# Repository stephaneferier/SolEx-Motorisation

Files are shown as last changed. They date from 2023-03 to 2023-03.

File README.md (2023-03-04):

# SolEx Motorisation (English version below)

Le Sol'Ex de Christian Buil est un "Explorateur solaire" qui permet d'imager le soleil dans une longueur d'onde souhaitée, allant du proche UV au proche IR.
La construction de ce spectroscope est détaillée sur son site internet: http://www.astrosurf.com/solex/sol-ex-objet.html
La partie traitement informatique du signal enregistré est confiée soit à i-Spec (programme écrit par Christian Buil), soit par Inti, programme développé par Valérie Desnoux. Ces deux programmes sont référencés sur le site Sol'Ex, et des mises à jour régulières sont publiées.
Un forum d'échange est aussi disponible à l'adresse : https://groups.io/g/Solex-project La communauté y est très active.

Nous vous présentons ici un appendice développé conjointement par Jean Brunet et Stéphane Ferier, qui permet de motoriser le Sol'Ex initial.
Le but ici est d'apporter une facilité à voyager parmi les raies spectrales qui composent le spectre solaire, au moyen d'un software développé pour Android/IOS, basé sur une page web gérée par le software. Des raies spectrales d'intérêt majeur y sont définies, et accessibles d'un simple clic. Le software permet outre les raies pré-programmées de sélectionner une longueur d'onde souhaitée et de demander au moteur d'orienter le réseau sur cette longueur d'onde. A l'inverse, il est aussi possible de visualiser une longueur d'onde (par retour de caméra d'acquisition), et de l'identifier sur l'affichage de la page web.

Le programme ainsi que les fichiers .stl de construction du support de motorisation sont "open-source", et toute amélioration est la bienvenue.
A cet effet, le fichier .rar contient tout le matériel nécessaire, y compris un fichier excel qui permet de trouver les paramètres de droite standard d'étalonnage.
En effet, le matériel fourni est optimisé pour un réseau de diffraction de 2400tr/mm; optiques 80/125mm constituant le Sol'Ex, ainsi que pour des roues dentées de motorisation d'un rapport de démultiplication 16 et 60 (GT-2) soit 3.75x. Si l'on souhaite utiliser un autre rapport, la droite d'étalonnage doit être adaptée en conséquence.

Outre le fichier .rar, vous trouverez aussi un fichier .pdf qui décrit en détails comment réaliser cette motorisation, comment monter le système sur le Sol'Ex, comment réaliser le montage électronique de pilotage, comment uploader le software dans l'ESP32 utilisé, ainsi que coment utiliser le software. Ce fichier .pdf est disponible en Français, et en Anglais.

# SolEx Motorization (English Version)

Christian Buil's Sol'Ex  is a "Solar Explorer" that allows you to image the sun in a desired wavelength, ranging from near UV to near IR.
The construction of this spectroscope is detailed on his website : http://www.astrosurf.com/solex/sol-ex-objet.html
The computer processing part of the recorded signal is entrusted either to i-Spec (program by  Christian Buil), or by Inti, program developed by Valérie Desnoux. These two programs are referenced on the Sol'Ex website, and regular updates are published.
An exchange forum is also available at: https://groups.io/g/Solex-project The community is very active.

We present here an appendix developed jointly by Jean Brunet and Stéphane Ferier, which allows to motorize the initial Sol'Ex .
The goal here is to provide an ease of travel among the spectral lines that make up the solar spectrum, by means of a software developed for Android/IOS, based on a web page managed by the software. Spectral lines of major interest are defined, and accessible within a simple click. In addition to the pre-programmed lines, the software allows you to  select a desired wavelength and ask the engine to orient the grating on this wavelength. Conversely, it is also possible to visualize a wavelength (by return of acquisition camera), and to identify it on the display of the web page.

The program as well as the .STL to build the motorization are "open-source", and any improvements are welcome.
For this purpose, the . RAR contains all the necessary material, including an Excel file  that allows you to find the standard calibration right settings.
Indeed, the equipment supplied is optimized for a diffraction grating of 2400lines/mm;  80/125mm optics constituting the Sol'Ex, as well as for gear wheels of motorization of a ratio of 16 and 60 (GT-2) or 3.75x. If another gear is to be used, the calibration line must be adjusted accordingly.

In addition to the . rar, you will also find a .pdf which describes in detail  how to make this engine, how to mount the system on the Sol'Ex, how to make the electronic control assembly, how to upload the software in the ESP32 used, as well as how to  use the software. This . pdf is available in French and English.

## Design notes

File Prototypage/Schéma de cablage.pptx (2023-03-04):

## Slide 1

Schéma de cablage des composants électroniques (Plaque de prototypage)

VCC au 3,3V
GND à la masse
SCL à GPIO22
SDA à GPIO 21

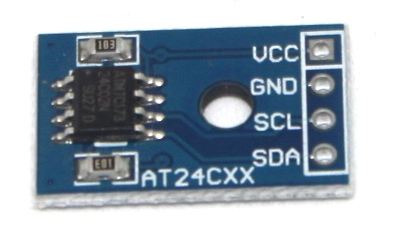
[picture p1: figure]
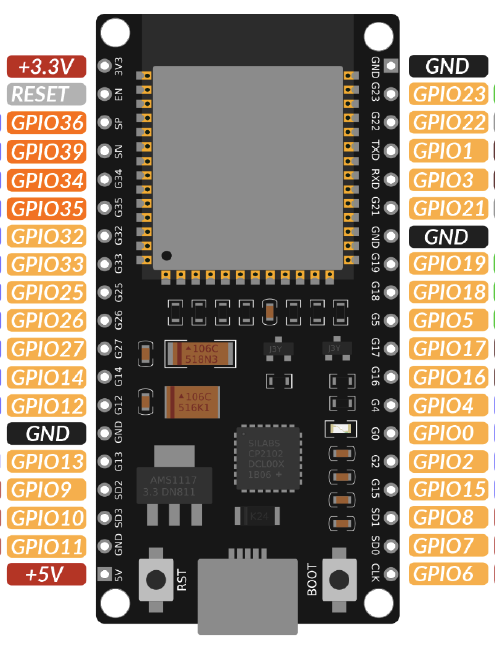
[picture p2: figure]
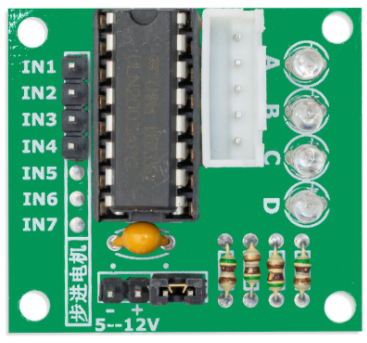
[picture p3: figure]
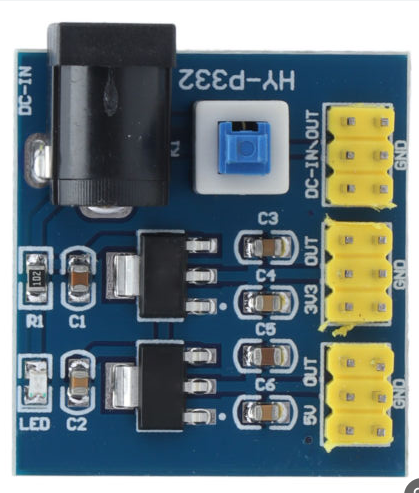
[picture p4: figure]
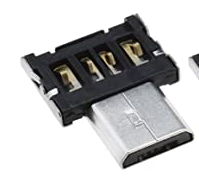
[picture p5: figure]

Pour alimenter l’ESP par l’USB, prévoir des fils pas trop fins!
Idem pour l’UNL2003. (même diamètre que ceux du moteur)

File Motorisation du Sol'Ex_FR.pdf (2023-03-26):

Motorisation du Sol’Ex (par Jean Brunet et Stéphane Ferier)

Bref historique :
Au début de l’aventure Sol’Ex, j’ai rapidement souhaité motoriser le spectroscope, afin de faciliter à l’utilisateur la recherche des bandes d’intérêt. En effet, la multitude de bandes du spectre solaire ne permet pas de trouver son chemin de manière aisée pour le débutant en spectroscopie. Le simple fait de rechercher la raie Hα peut prendre un temps précieux, surtout lorsque le matériel est à remettre en station si l’on ne dispose pas d’un abri astro poste fixe. Poser la monture, l’orienter correctement pour pouvoir réaliser le suivi solaire (mise en station de jour) assemblage de la lunette et du Sol’Ex ; recherche de la raie d’intérêt … Tout cela peut prendre beaucoup de temps et décourager à sortir le matériel si le ciel est nuageux et offre peu de « fenêtres de tir » !
L’idée était alors de motoriser la rotation du réseau, et de pouvoir enregistrer l’écart entre l’ordre 0 et la raie Hα. Réaliser une droite standard sur les raies d’intérêt majeures. Par la suite, calculer le nombre de pas moteur à réaliser pour pouvoir atteindre d’autres raies d’intérêt, en prenant en compte une approximation de linéarité dans la distribution des raies d’intérêt et des pas moteur pour les atteindre.

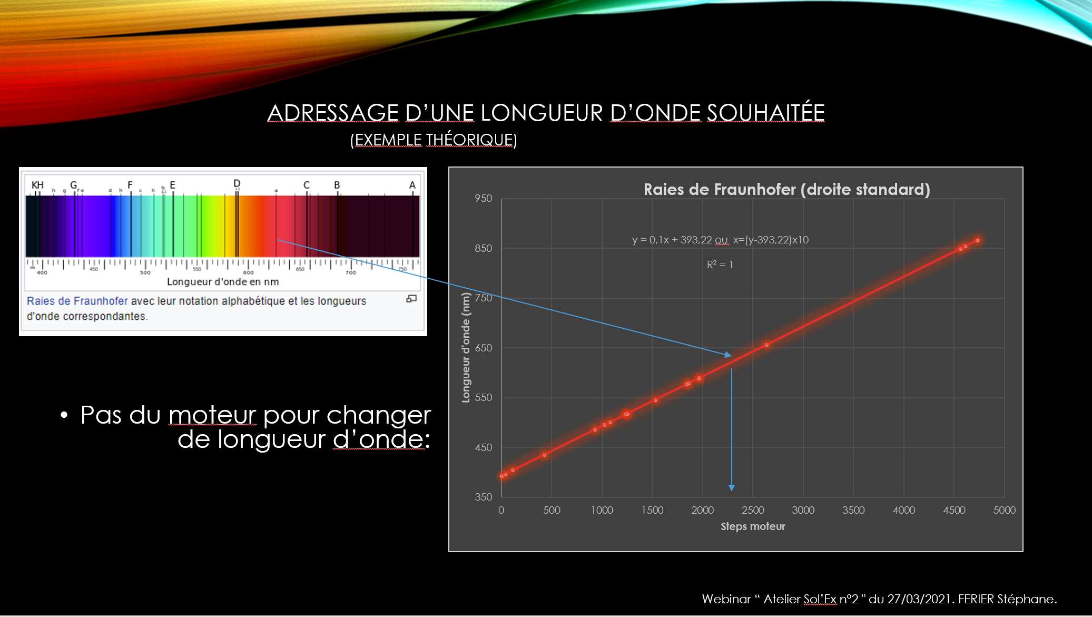
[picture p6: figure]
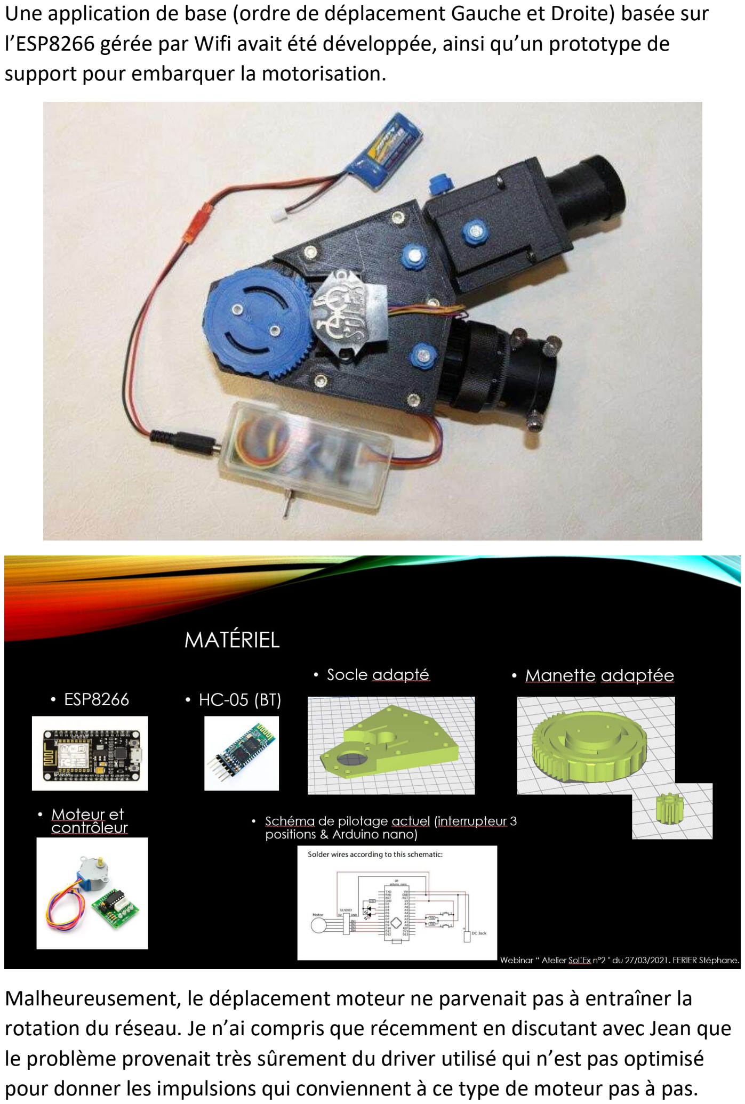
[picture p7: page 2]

Une application de base (ordre de déplacement Gauche et Droite) basée sur l’ESP8266 gérée par Wifi avait été développée, ainsi qu’un prototype de support pour embarquer la motorisation.

Malheureusement, le déplacement moteur ne parvenait pas à entraîner la rotation du réseau. Je n’ai compris que récemment en discutant avec Jean que le problème provenait très sûrement du driver utilisé qui n’est pas optimisé pour donner les impulsions qui conviennent à ce type de moteur pas à pas.

Un second prototype est alors envisagé, utilisant une courroie plutôt qu’un entraînement dent contre dent utilisé pour ce premier essai.
Dans le but de rendre le système le plus compact possible, j’ai alors redessiné la partie supérieure du corps principal du Sol’Ex pour y intégrer le moteur.

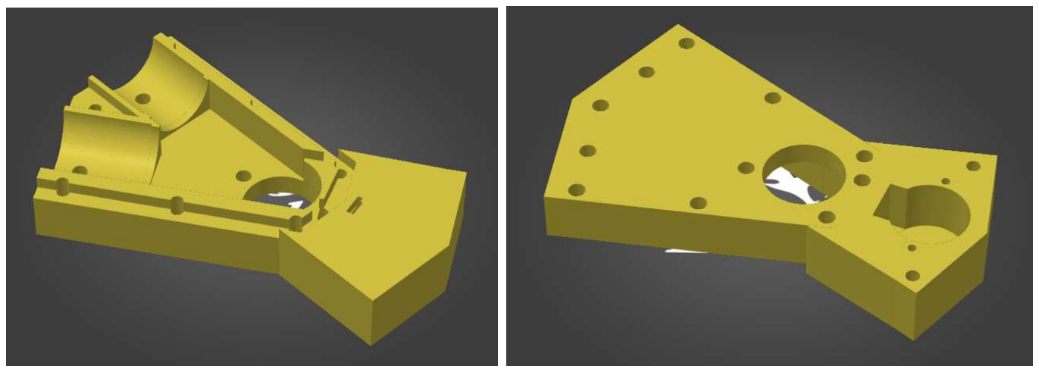
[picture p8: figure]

Cet essai, bien que plus « propre » intégrant le moteur dans l’axe du Sol’Ex n’a pas permis à ce moment d’améliorer la problématique de l’entraînement. (On sait maintenant pourquoi !!). Je désespérais de trouver une solution fonctionnelle.
De son côté, l’idée de la motorisation avait aussi germé dans l’esprit de Jean Brunet ! Son premier prototype nous était partagé pour la Saint Nicolas (… et oui, je suis Belge, et chez nous, c’est le jour des cadeaux )

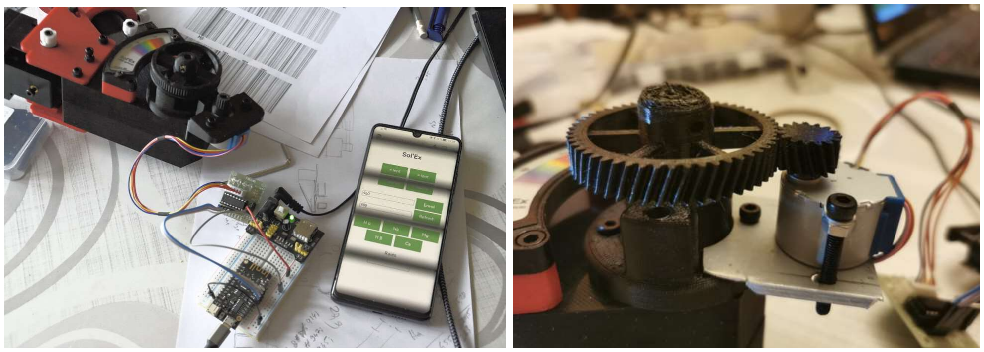
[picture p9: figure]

C’est alors que nous avons commencé à échanger sur le sujet offline, car dans nos conversations, il venait avec une idée géniale à mes yeux, revenir à un boîtier additionnel, utilisant des roulements à billes et un axe d’entraînement.

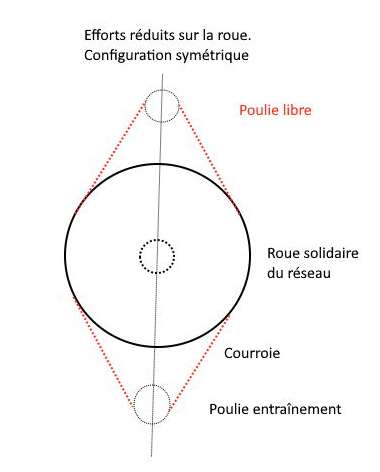
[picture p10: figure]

Les contraintes physiques de tension sur l’axe du porte réseau en ont profité pour disparaître … De plus, Jean avait aussi réalisé un software parfaitement fonctionnel et apportant directement des « touches préprogrammées » pour aligner les raies majeures ! Par la suite, la poulie libre du schéma ci-dessus n’apportant rien de particulier a été enlevée.
Mon bonheur était fait …
Voici son boitier en version de test :

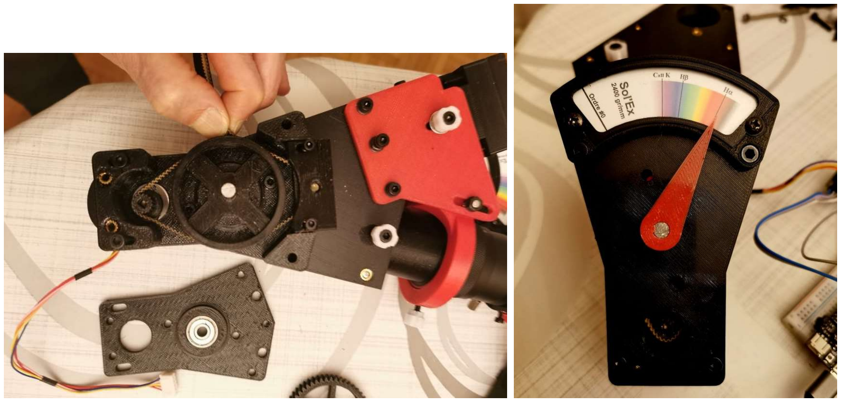
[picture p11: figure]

Il ne restait plus qu’à optimiser les pièces pour une réalisation plus aisée, utilisant deux poulies et une courroie, facilement trouvables par internet.

Pendant ce temps, Jean peaufinait la partie électronique en réalisant un PCB de test, et un boitier adapté à son montage électronique. De mon côté, j’adaptais le programme à une roue dentée commerciale de 60 dents.
Nous vous proposons en annexes le fruit de notre travail commun, comprenant un montage mécanique simple, et deux options possibles pour la partie électronique, basées sur soit un PCB à graver, soit une plaque de prototypage comme illustré sur cette image.

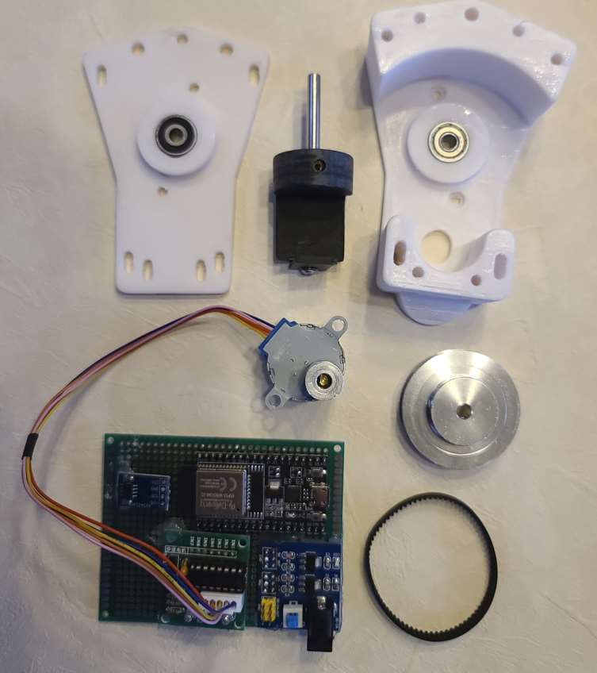
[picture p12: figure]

La programmation de la motorisation est aussi expliquée en détails plus bas. Concernant le matériel à vous procurer, tout se trouve aussi plus bas dans ce document, y compris des liens proposés pour trouver les pièces à commander.

Impressions 3D, montage électronique : Préambule.
Comme dit un peu plus haut, annexés à ce document, vous trouverez les fichiers .STL nécessaires qui vous permettront d’imprimer les bâtis inférieur et supérieur, ainsi que le nouveau support réseau adapté au montage.
Point d‘attention suivant : il n’est pas donné à tout un chacun de savoir imprimer un PCB (carte de support pour les composants électroniques).
Vous trouverez donc deux options possibles : soit le plan pour imprimer votre PCB et y monter les composants électroniques, ainsi qu’un boitier, soit le schéma pour monter les composants directement sur une plaque de prototypage. L’alimentation se fait par le port USB de l’ESP. C’est lui seul qui alimente aussi le moteur.

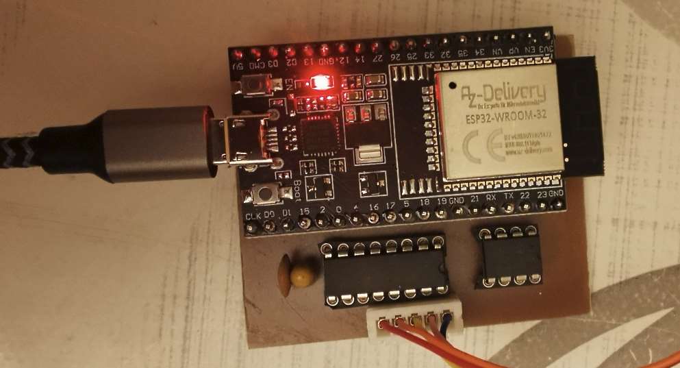
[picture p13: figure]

Dans le kit « prototypage », la partie électronique sera disposée sur une plaque de prototypage. Comme vous pourrez y disposer les composants à votre goût, il n’y a pas ici de fichiers STL pour le boitier.
Un fichier PPT reprend les connections à réaliser entre les composants. L’avantage ici, c’est que sans les compétences pour réaliser le PCB, vous pouvez quand même réaliser la motorisation de votre Sol’Ex.
Autre avantage de l’alimentation proposée ici, c’est que vous pouvez alimenter idéalement en 12V (de 8 à 12V en réalité, mais je conseille le 12V), et que le module dispose d’un bouton « on/off » intégré. La réalisation d’un boitier pourra dès lors utiliser cette fonction supplémentaire. Attention que pour bien fonctionner, l’ESP doit impérativement être alimenté par l’USB (dans les deux options).

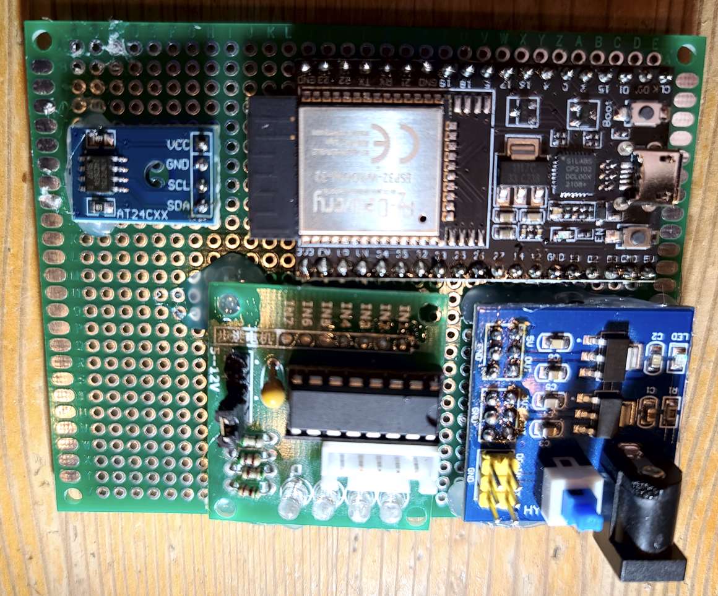
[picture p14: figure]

Pour l’impression des pièces 3D, il y a toujours le PETG, mais j’ai préféré utiliser le PLA+ ou PLA + Carbone de chez Sunlu. Ce matériau est plus dur une fois refroidi. Le PLA+ s’imprime à 225°c, sur un lit à 80°c. Afin d’améliorer l’adhérence lors de l’impression, utilisez de la laque 3D sur votre vitre d’impression. Vous pouvez aussi tester avec de la laque pour cheveux, mais celle-ci adhère moins que celle prévue pour la 3D.

Les pièces à imprimer en 3D :
La partie mécanique est composée :
- D’un nouveau support réseau adapté pour y insérer un axe 5mm long de 40mm (ou 50mm si vous souhaitez utiliser le vernier de Xavier audessus de la motorisation), qui servira à l’entraînement. Afin de fixer l’axe dans le porte réseau, on utilise un écrou Ruthex M3 et une vis sans tête. Il est aussi possible de coller l’axe dans le porte réseau, mais attention que l’axe métallique doit impérativement être bien vertical !!
- Le bâti inférieur qui recevra un roulement à billes et les poulies/courroie d’entraînement ;
- Le bâti supérieur qui recevra lui aussi un roulement à billes.
Coupe 3D des différentes pièces à imprimer :

Montage du kit de motorisation :
Comme nous avons déjà réalisé notre Sol’Ex, le plus difficile est loin derrière nous ! Il faudra donc ici remplacer précautionneusement le porte réseau initial par celui du kit.
La première chose à faire, avant de mettre le réseau en place, c’est de fixer l’axe dans le porte réseau. Vous pouvez le coller avec une colle deux composants, ou utiliser un filet Ruthex 3mm et une vis sans tête, à insérer dans l’orifice perpendiculaire à l’axe de rotation du porte réseau.

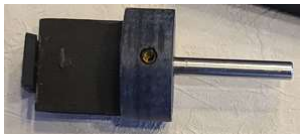
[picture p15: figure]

Le réseau sera ensuite disposé sur le porte réseau, puis le tout inséré dans le corps du Sol’Ex.
Ensuite, on vient disposer le bâti inférieur autour de l’axe et on le solidarise au Sol’Ex par les vis qui étaient utilisées pour fixer la manette réseau de Christian.

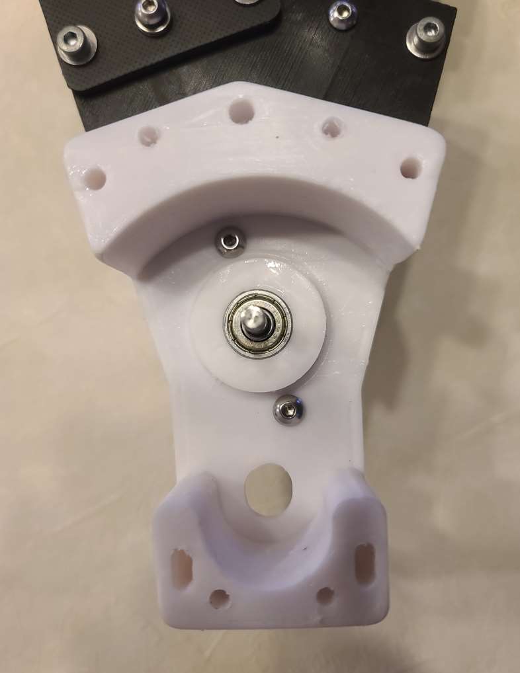
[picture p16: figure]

On dispose ensuite la poulie principale sur l’axe. Ici aussi, elle dispose de vis sans tête pour rendre l’axe et la poulie solidaires. Pensez à repérer l’orientation de l’ordre zéro du réseau par un trait sur le bâti et la poulie. On dispose ensuite la poulie qui s’adapte au moteur, ainsi que la courroie avant de fixer et tendre légèrement la courroie en fixant le moteur sur le bâti inférieur. Il se fixe à l’extérieur du montage.

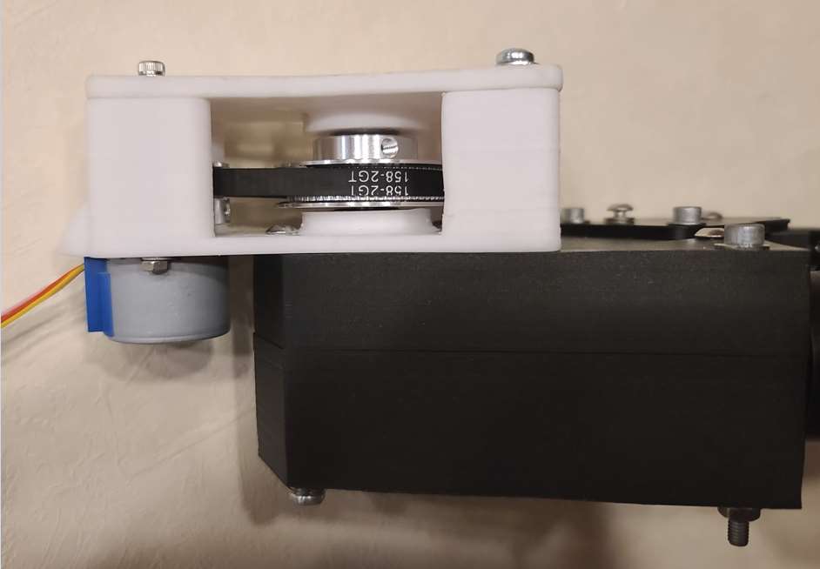
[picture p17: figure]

Comme on peut le voir sur cette image, les vis de maintien du moteur passent au travers des deux bâtis. On voit aussi ici les logements de vis sans tête de la poulie.
Le montage refermé ressemble à ceci :

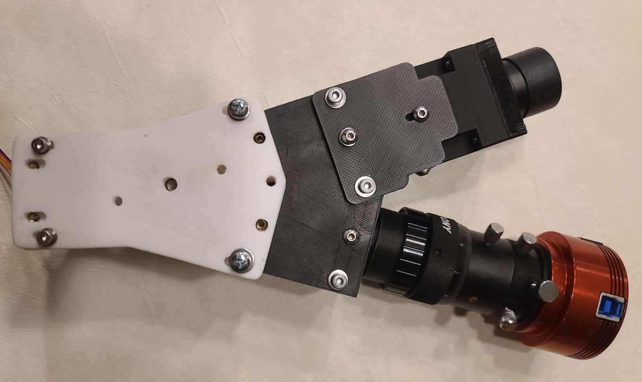
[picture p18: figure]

Deux longues vis M4 complètent le montage et solidarisent encore un peu plus l’ensemble. Le vernier de Xavier peut être aussi ajouté, afin de garder un repère visuel sur la position du réseau. Dans ce cas, l’axe de rotation devra dépasser du montage, afin de pouvoir y fixer une aiguille qui est à disposition dans le kit RAR.

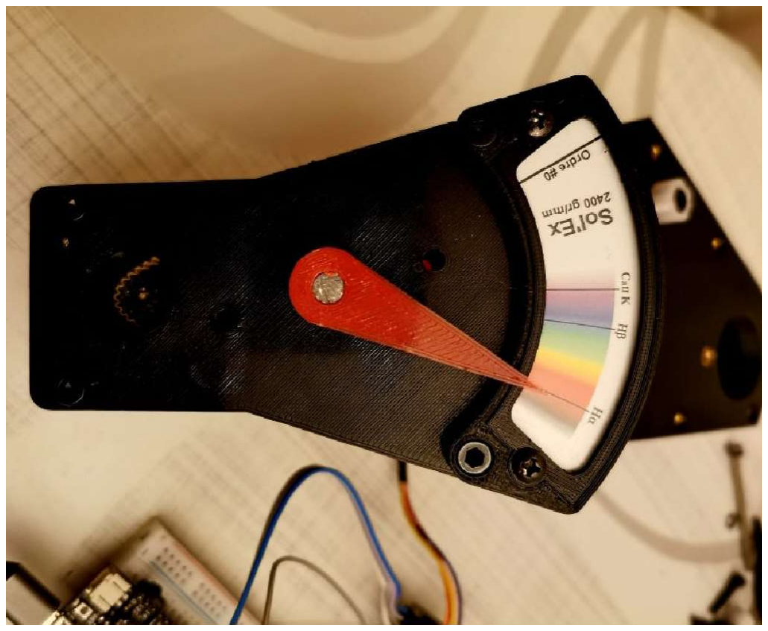
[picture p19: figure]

Réglage de l’inclinaison de l’axe :
Dans certains cas, il se peut que l’image renvoyée par le réseau vers la caméra ne soit pas bien centrée … Ce défaut d‘alignement peut être corrigé en ajoutant une épaisseur de papier collant derrière le réseau pour l’incliner légèrement… Mais rassurez-vous, je n’en ai pas eu besoin.

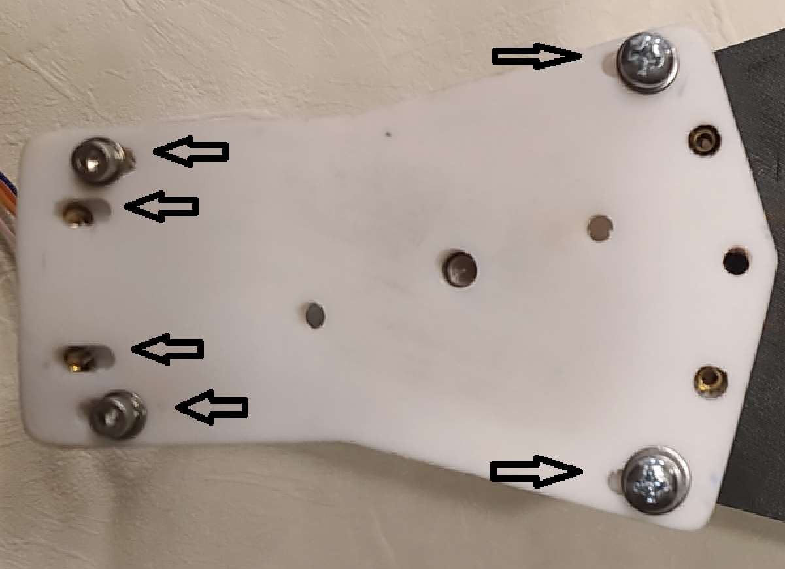
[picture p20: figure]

La partie mécanique est terminée !!

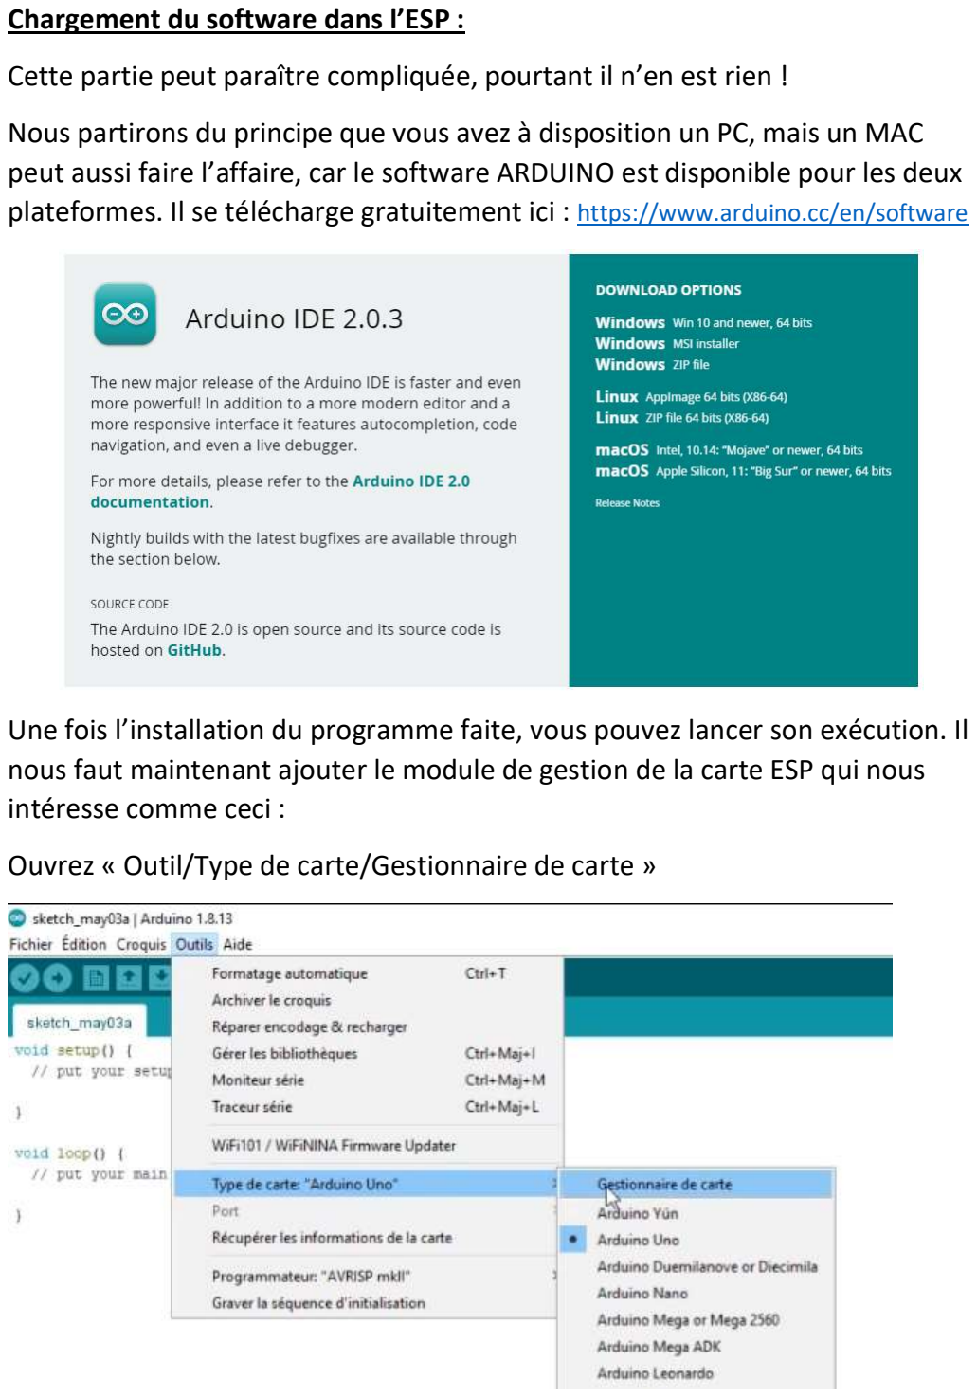
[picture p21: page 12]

Chargement du software dans l’ESP :
Cette partie peut paraître compliquée, pourtant il n’en est rien !
Nous partirons du principe que vous avez à disposition un PC, mais un MAC peut aussi faire l’affaire, car le software ARDUINO est disponible pour les deux plateformes. Il se télécharge gratuitement ici : https://www.arduino.cc/en/software

Une fois l’installation du programme faite, vous pouvez lancer son exécution. Il nous faut maintenant ajouter le module de gestion de la carte ESP qui nous intéresse comme ceci :
Ouvrez « Outil/Type de carte/Gestionnaire de carte »

Tapez « ESP32 », vous pouvez installer la version 1.0.6

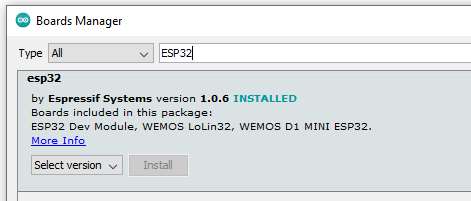
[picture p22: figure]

Sélectionnez ensuite ESP32 Dev Module :

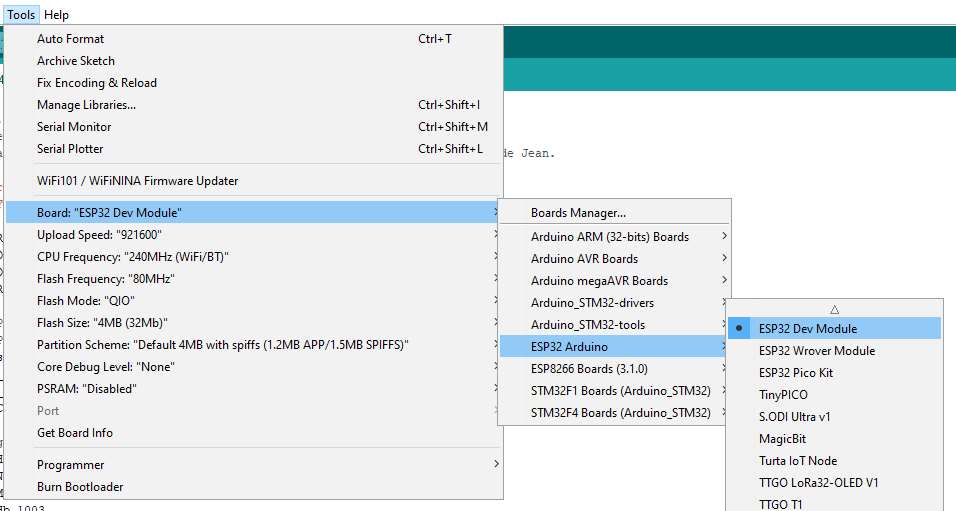
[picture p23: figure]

Vous déposez le dossier « Arduino » qui se trouve dans votre fichier RAR dans le dossier « Documents ».

Dans le menu « Fichier/Préférences » de l’application Arduino, indiquez le chemin du dossier où vous souhaitez déposer les fichiers de travail. Dans mon cas, j’ai choisi « Documents/Arduino » :

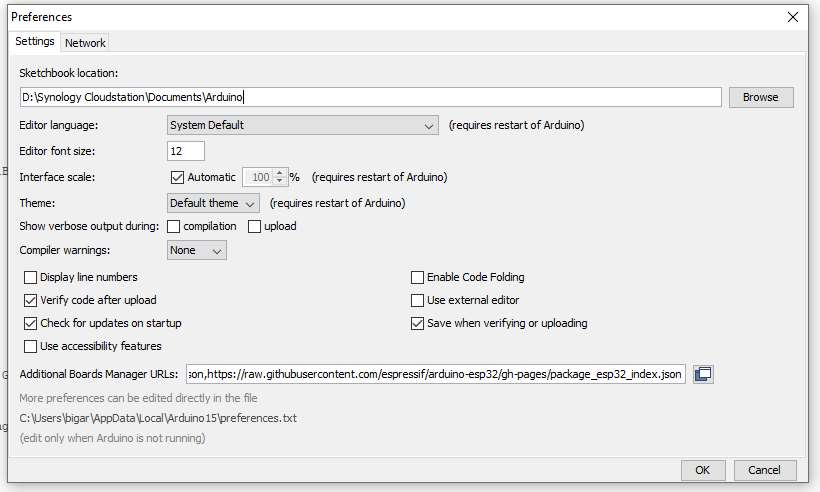
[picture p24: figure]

Tant qu’on est dans cette fenêtre, profitez de l’occasion pour ajouter dans
« Gestionnaire URL de carte additionnelles » les lignes suivantes, qui pourront vous servir pour d’autres applications Arduino :

https://dl.espressif.com/dl/package_esp32_index.json

http://arduino.esp8266.com/stable/package_esp8266com_index.json

https://raw.githubusercontent.com/espressif/arduino-esp32/gh-pages/package_esp32_index.json
Vous pouvez refermer cette fenêtre.
Chargez maintenant le fichier « ESP_SolEx .INO» situé dans le dossier « Documents/Arduino/ »


Connectez l’ESP32 par un câble USB à votre ordinateur, une led rouge doit s’allumer en continu sur l’ESP.
Vérifiez sur quel « port Com » l’ESP est connecté à votre PC/MAC :
Clic droit sur la fenêtre Windows ; Device Manager :

puis :
Dans mon cas, c’est le port « Com5 » qui est assigné à l’ESP. Vérifiez ensuite l’équivalence de connexion ici :


Vous êtes maintenant prêts à téléverser le programme dans l’ESP. On vérifie que tout est prêt en cliquant sur le bouton « v » ici :

La console devrait vous indiquer ceci :

Dans ce cas, le téléversement peut s’effectuer en appuyant sur le bouton « boot » de l’ESP et en cliquant sur la flèche :

La console nous renseigne du statut de téléversement, et conclut par :


Bravo, vous avez programmé votre ESP. On va pouvoir tester tout cela …

Réglage de position du moteur / ordre zero :

Alimentons notre montage …

L’interface est appelée après connexion par WiFi au serveur Sol’Ex. Le password par défaut est : solex1234

Pour appeler l’interface, entrez l’adresse http suivante : 192.168.4.1

Si cette adresse est déjà utilisée par votre réseau, vous trouverez celle définie par votre DNS serveur pour le Sol’Ex ici : (ouvrez « Propriétés » de SolEx dans vos connections réseau WiFi)


L’interface apparaît comme suit :


Cochez la case « réglage », puis cliquez sur la case verte/bleue « Ordre 0 » :

Cela a pour effet de vider le champ « Raie (nm) » et de mettre le nombre de pas à zéro.

Utilisez ensuite les flèches pour ramener le réseau en position « ordre 0 »

… et ajustez précisément l’ordre 0 au centre de la fenêtre de votre caméra, dans la zone que vous utiliserez lors des scans du soleil.

Lorsque c’est fait, décochez la case « Réglage », afin de tester les longueurs d’ondes programmées.

### 3 zones de sélections sont possibles pour faire pivoter le réseau vers la longueur d’onde

cible :

Les cases préprogrammées (Hα, Na, Mg, Hß, Ca) ;

La zone à choix multiple et le bouton « Sélection » (30 raies d’intérêt y sont encodées) ;

Le champ libre et le bouton « Envoi ».

Selon votre choix, le moteur fait tourner le réseau jusqu’à atteindre la longueur d’onde de votre choix. L’affichage indique alors la longueur d’onde centrée et le nombre de pas moteur de cette position.

Vous avez ensuite le choix de changer de longueur d’onde d’intérêt en utilisant l’un des 3 modes de sélection : les cases ou champs préprogrammés, ou l’utilisation de la boite d’envoi :

En appuyant sur « Envoi », le moteur diminuera ou augmentera le nombre de pas depuis la position actuelle vers votre nouvelle cible par incrément de plusieurs pas moteur, jusqu’à approcher votre cible (mais ne se positionne pas avec précision)

Pour affiner la position, vous pouvez alors utiliser les boutons de direction jusqu’à atteindre votre cible avec plus de précision :

La flèche | incrémente de 2 pas moteur ; | 10 pas ; | 25 pas.

Si vous arrêtez la motorisation en coupant son alimentation, la dernière position est mémorisée dans l’EEPROM, de sorte que si vous n’avez pas modifié manuellement la position du réseau, lors du rallumage du système, les informations sont reprises là où elles ont été interrompues.

Il peut toutefois être utile (ou souhaité) de vérifier cette position. Dans ce cas, l’appui sur le bouton « Ordre 0 » fera revenir le réseau vers l’ordre zéro. Attention de ne pas cocher la case réglage dans ce cas.

Nota Bene : Les programmations enregistrées dans le fichier « ESP_SolEx.INO » que vous avez uploadé sur l’ESP32 sont valables sans modification pour la seule utilisation d’un réseau 2400tr/mm, en combinaison avec les roues dentées préconisées dans le système proposé :

- Poulie principale de 60-GT2, poulie moteur de 16-GT2 et courroie GT-2

Bon amusement !

Jean et Stéphane.

Matériel utilisé :
Partie mécanique :
PLA+ (Sunlu) pour les pièces à imprimer (lit à 80°c ; tête d’impression à 225°c) ;

### 5 Ruthex M3 & 2 Ruthex M4 ; rondelles pour M3 et M4 2 vis M4 50mm ; 4 vis M3 15mm et 2 vis M3 40mm + écrous 1 vis sans tête M3 (pour fixer l’axe dans le porte réseau

### 1 axe 5mm diamètre, longueur 40mm : https://www.amazon.fr/dp/B07P45W61W

### 2 roulements à billes 625ZZ : https://www.amazon.fr/dp/B079DKGWS9

### 1 moteur 28BYJ-48 5V (voir plus bas pour référence)

### 1 poulie 60 dents https://www.amazon.fr/dp/B07N65GCL6

1 poulie 16 dents https://www.amazon.fr/DollaTek-aluminium-al%C3%A9sage-largeur-Imprimante/dp/B07DK3DCMS

### 1 courroie 158 dents https://www.amazon.fr/dp/B07D923SDS

Partie électronique :

ESP32-WROOM-32 Dev kit C4: https://www.amazon.fr/dp/B08BTS62L7

ULN2003 & moteur 28BYJ-48 5V: https://www.amazon.fr/HUABAN-moteurs-28BYJ-48-module-

ULN2003/dp/B08B4J33HX/ref=sr_1_6

Connecteur USB pour alimentation : https://www.amazon.fr/dp/B0BQMWCSFL

EEPROM : https://www.amazon.fr/dp/B07RHMPRK1

Module d’alimentation: https://www.amazon.fr/DollaTek-dalimentation-Conversion-Tension-Multi-

Sortie/dp/B07DK4NTH3

Carte de prototypage 7x9cm : https://www.amazon.fr/HeyNana-prototype-perfor%C3%A9e-circuit-

Prototype/dp/B0924S5RD6
Cable USB pour programmer l’ESP ;

Alimentation 12V ou USB en fonction du montage choisi.

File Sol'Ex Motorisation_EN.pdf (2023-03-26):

Motorization of Sol'Ex (by Jean Brunet and Stéphane Ferier)

Brief history:
At the beginning of the Sol'Ex adventure, I quickly wanted to motorize the spectroscope, in order to facilitate the user's search for bands of interest. Indeed, the multitude of bands of the solar spectrum does not make it easy to find its way for the beginner in spectroscopy. The simple fact of searching for the Hα line can take precious time, especially when the equipment is to be put back in station if one does not have a fixed astro shelter. Place the mount, orient it correctly to be able to carry out solar monitoring (day stationing) assembly of the scope and Sol'Ex; search for the line of interest ... All this can be time-consuming and discouraging to take out the equipment if the sky is cloudy and offers few "shooting windows"!
The idea was then to motorize the rotation of the grating, and to be able to record the difference between the order 0 and the Hα line. Make a standard line on the lines of major interest. Subsequently, calculate the number of motor steps to be achieved to be able to reach other lines of interest, taking into account an approximation of linearity in the distribution of lines of interest and motor steps to reach them.


A basic application (left and right movement order) based on the ESP8266 managed by Wifi has been developed, as well as a prototype support to embed the engine.


Unfortunately, the engine displacement was unable to cause the network to rotate. I only recently understood by talking with Jean that the problem was most likely due to the driver used which is not optimized to give the impulses that suit this type of stepper motor.
A second prototype is then envisaged, using a belt rather than a tooth-to-tooth drive used for this first test.

In order to make the system as compact as possible, I then redesigned the upper part of the main body of the Sol'Ex to integrate the engine.


This test, although "cleaner" integrating the engine in the axis of the Sol'Ex did not allow at this time to improve the problem of the drive. (We now know why!!). I was desperate to find a working solution.
From his side, the idea of motorization had also germinated in the mind of Jean Brunet! His first prototype was shared with us for Saint Nicolas (... and yes, I'm Belgian, and at home, it's gift day )


That's when we started talking about the topic offline, because in our conversations, he came up with a brilliant idea to my eyes, to go back to an additional box, using ball bearings and a drive axis.


The physical constraints of tension on the axis of the grating support took advantage of this to disappear ... In addition, Jean had also made a perfectly functional software and directly bringing "pre-programmed keys" to align the major lines! Subsequently, the free pulley of the diagram above bringing nothing special was removed.
My happiness was made ...
Here is its case in test version:


All that remained was to optimize the parts for easier realization, using pulleys and a belt, easily found by internet.

During this time, Jean was refining the electronic part by making a test PCB, and a box adapted to its electronic assembly. By my side, I updated the software for use with commercial wheel of 60 teeth.
We offer in appendices the fruit of our joint work, including a simple mechanical assembly, and two possible options for the electronic part, based on either a PCB to be engraved, or a prototyping plate as illustrated in this image.


The programming of the engine is also explained in detail below. Regarding the equipment to be purchased, everything is also found further down in this document, including links to find the parts to order.

3D printing, electronic editing : Preamble.
As said a little above, annexed to this document, you will find the . STL files necessary that will allow you to print the lower and upper frames, as well as the new grating support suitable for mounting.
Next point of attention: it is not given to everyone to know how to print a PCB (support board for electronic components).
You will therefore find two possible options: either the plan to print your PCB and mount the electronic components, as well as a box, or the diagram to mount the components directly on a prototyping plate. Power is supplied through the USB port of the ESP. It is the only way to consider to power the engine.

In the "prototyping" kit, the electronic part will be placed on a prototyping plate. As you can arrange the components to your willing, there are no STL files for the case here.
A PPT file lists the connections to be made between the components. The advantage here is that without the skills to make the PCB, you can still realize the motorization of your Sol'Ex.
Another advantage of the power supply offered here is that you can ideally supply 12V (from 8 to 12V in reality, but I recommend 12V), and that the module has an integrated "on / off" button. The realization of a box can then use this additional function. Be careful that to work properly, the ESP must be powered by USB (in both options).


For the printing of 3D parts, there is always PETG, but I preferred to use PLA+ or PLA + Carbon from Sunlu. This material is harder once cooled. The PLA+ is printed at 225°c, on a bed at 80°c. To improve adhesion when printing, use 3D lacquer on your printing glass. You can also test with hair spray, but it adheres less than the one intended for 3D.

Parts to be printed in 3D:
The mechanical part is composed of:
- A new network support adapted to insert a 5mm long axis of 40mm (or 50mm if you want to use Xavier's vernier above the motorization), which will be used for axis rotation. In order to fix the axis in the grating holder, a Ruthex M3 nut and a headless screw are used. It is also possible to glue the axis in the grating holder, but be careful that the metal axis must be perfectly vertical!
- The lower frame that will receive a ball bearing and pulleys/drive belt;
- The upper frame which will also receive a ball bearing.
3D section of the different parts to be printed:


Assembly of the motorization kit:
As we have already made our Sol'Ex, the most difficult is far behind us! It will therefore be necessary here to carefully replace the initial network port by that of the kit.
The first thing to do, before setting up the grating, is to fix the axis in the grating support. You can glue it with a two-component glue, or use a 3mm Ruthex and a headless screw, to be inserted into the hole perpendicular to the axis of rotation of the network holder.


The grating will then be placed on the grating holder, then all inserted into the body of the Sol'Ex.
Then, the lower frame is placed around the axis and it is secured to the Sol'Ex by the screws that were used to fix Christian's grating wheel.


The main pulley is then placed on the axis. Here too, it has headless screws to make the axle and pulley solid. Remember to identify the orientation of the zero order of the network by a line on the frame and pulley. We then arrange the pulley that adapts to the engine, as well as the belt before fixing and slightly tightening the belt by fixing the motor on the lower frame. It attaches to the outside of the mount.


As can be seen in this image, the motor holding screws pass throughtwo frames. We also see here the headless screw housings of the pulley. The closed ensemble looks like this:


Two long M4 screws complete the assembly and solidify the whole thing a little more. Xavier's vernier can also be added, in order to keep a visual reference on the position of the network. In this case, the axis of rotation will have to protrude from the assembly, in order to be able to attach a needle that is available in the RAR kit.


Adjusting the axis tilt:
In some cases, it may be that the image sent back by the grating to the camera is not well centered ... This misalignment can be corrected by adding small tape behind the grating, in order to incline it as needed ... But rest assured, I didn't need it.


The mechanical part is over!!


Loading the software into the ESP:
This part may seem complicated, but it is not!
We will assume that you have a PC at your disposal, but a MAC can also do the trick, because ARDUINO software is available for both platforms. It can be
downloaded for free here: https://www.arduino.cc/en/software

Once the program is installed, you can start running it. Now we need to add the ESP card management module that interests us like this:
Open "Tool/Card Type/Card Manager"

Type "ESP32", you can install version 1.0.6


Then select ESP32 Dev Module:

You drop the "Arduino" folder that is in your RAR file into the "Documents" folder.

In the "File/Preferences" menu of the Arduino application, specify the path of the folder where you want to deposit the working files. In my case, I chose "Documents/Arduino":


While we are in this window, take the opportunity to add in "Additional Board URL Manager" the following lines, which can be used for other Arduino applications:


https://dl.espressif.com/dl/package_esp32_index.jsonhttp://arduino.esp8266.com/stable/package_esp8266com_index.jsonhttps://raw.githubusercontent.com/espressif/arduino-esp32/gh-pages/package_esp32_index.json
You can close this window.
Now load the file "ESP_SolEx . INO" located in the "Documents/Arduino/" folder


Connect the ESP32 via a USB cable to your computer, a red LED should light up continuously on the ESP.
Check which "Com port" the ESP is connected to your PC/MAC:
Right click on the Windows window; Device Manager:

then:
In my case, it is the port "Com5" that is assigned to the ESP. Then check the connection equivalence here:


You are now ready to upload the program to the ESP.
We check that everything is ready by clicking on the "v" button here:

The console should tell you this:

In this case, the upload can be done by clicking the “boot” button of the ESP as well as on the arrow below:

The console informs us of the upload status, and concludes with:


Congratulations, you have programmed your ESP. We will be able to test all this ...

Motor position adjustment / zero order:

Let's feed our assembly ...

The interface is called after connecting by WiFi to the Sol'Ex server. The default password is: solex1234

To call the interface, enter the following http address: 192.168.4.1

If this address is already used by your network, you will find the one defined by your DNS server for Sol'Ex here: (open SolEx "Properties" in your WiFi network connections)


The interface appears as follows:

Check the "setting" box, then click the green/blue "Order 0" box:

This has the effect of emptying the "Line (nm)" field and setting the number of steps to zero.

Then use the arrows to return the grating to the "order 0" position

... And precisely adjust the order 0 in the center of the window of your Camera, in the area you will use when scanning the sun.

When this is done, uncheck the "Setting" box to test the programmed wavelengths.

### 3 selection zones are possible to rotate the grating to the target wavelength:

Preprogrammed boxes (Hα, Na, Mg, Hß, Ca);

The multiple choice area and the "Selection" button (30 lines of interest are encoded );

The free field and the "Send" button.


Depending on your choice, the motor rotates the grating until it reaches the wavelength of your choice. The display then indicates the centered wavelength and the number of motor steps of this position.

You then have the choice to change the wavelength of interest using one of the 3 selection modes: the pre-programmed boxes or fields, or the use of the outbox:

By pressing "Send", the engine will decrease or increase the number of steps from the current position to your new target in increments of several engine steps, until it approaches your target (but does not position itself accurately)

To refine the position, you can then use the arrow buttons until you reach your target more accurately:

The arrow | increments by 2 motor steps; 10 steps; | 25 steps.

If you stop the engine by turning off its power, the last position is stored in the EEPROM, so that if you have not manually changed the position of the grating, when the system is turned back on, the information is picked up where it was interrupted.

However, it may be useful (or desired) to check this position. In this case, pressing the "Order 0" button will return the grating to order zero. Be careful not to check the setting box in this case.

Note: The programs recorded in the "ESP_SolEx.INO" file that you uploaded to the ESP32 are valid without modification for the sole use of a 2400 lines / mm grating, in combination with the gear wheels recommended in the proposed system:

- 60-GT2 main pulley, 16-GT2 motor pulley and GT-2 belt

Have fun!

Jean and Stéphane.

Material used:
Mechanical part:
PLA+ (Sunlu) for parts to be printed (bed at 80°c; print head at 225°c);

### 5 Ruthex M3 & 2 Ruthex M4 ; washers for M3 and M4 2 x M4 50mm screws; 4 screws M3 15mm and 2 screws M3 40mm + nuts 1 M3 headless screw (to fix the axis in the network holder

### 1 axis 5mm diameter, length 40mm: https://www.amazon.fr/dp/B07P45W61W

### 2 x 625ZZ ball bearings: https://www.amazon.fr/dp/B079DKGWS9

### 1 motor 28BYJ-48 5V (see below for reference)

### 1 pulley 60 teeth https://www.amazon.fr/dp/B07N65GCL6

1 pulley 16 teeth https://www.amazon.fr/DollaTek-aluminium-al%C3%A9sage-largeur-Imprimante/dp/B07DK3DCMS

### 1 belt 158 teeth https://www.amazon.fr/dp/B07D923SDS

Electronic part:

ESP32-WROOM-32 Dev kit C4: https://www.amazon.fr/dp/B08BTS62L7

ULN2003 & 28BYJ-48 5V motor: https://www.amazon.fr/HUABAN-moteurs-28BYJ-48-module-

ULN2003/dp/B08B4J33HX/ref=sr_1_6

USB connector for power: https://www.amazon.fr/dp/B0BQMWCSFL

EEPROM : https://www.amazon.fr/dp/B07RHMPRK1

Power module: https://www.amazon.fr/DollaTek-dalimentation-Conversion-Tension-Multi-Sortie/dp/B07DK4NTH3

Prototyping board 7x9cm: https://www.amazon.fr/HeyNana-prototype-perfor%C3%A9e-circuit-

Prototype/dp/B0924S5RD6
USB cableto program the ESP;

12V or USB power supply depending on the chosen assembly.

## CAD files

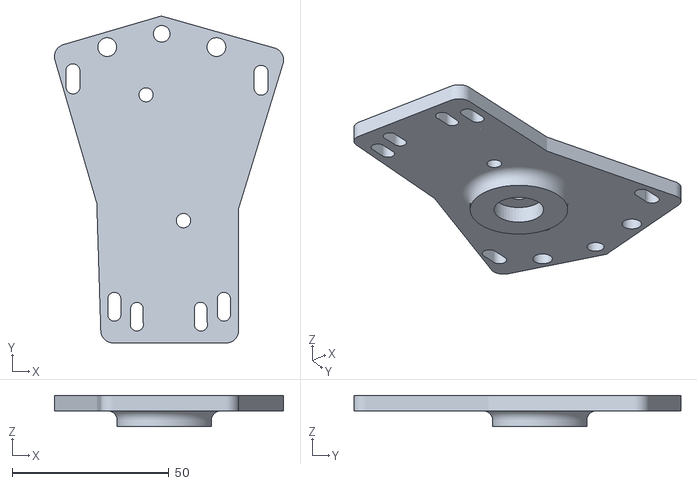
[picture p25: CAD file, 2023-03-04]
bati_supérieur.stl
73.2 x 104.4 x 10.0

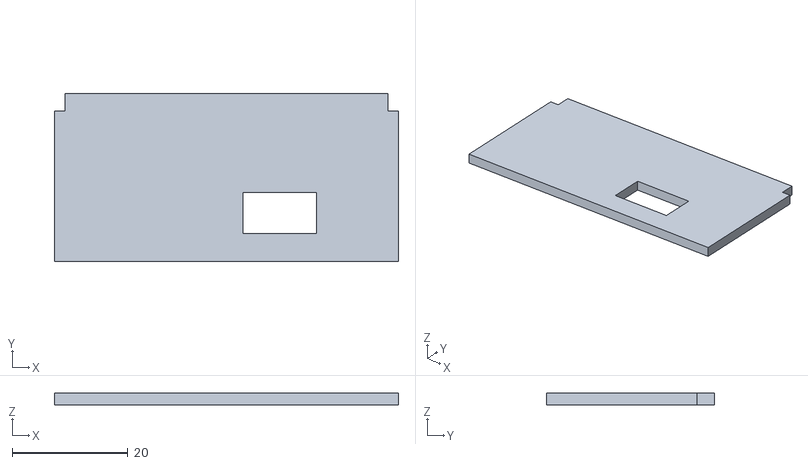
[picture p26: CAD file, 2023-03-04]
Boitier pour PCB imprimé/face.stl
59.4 x 29.0 x 2.00

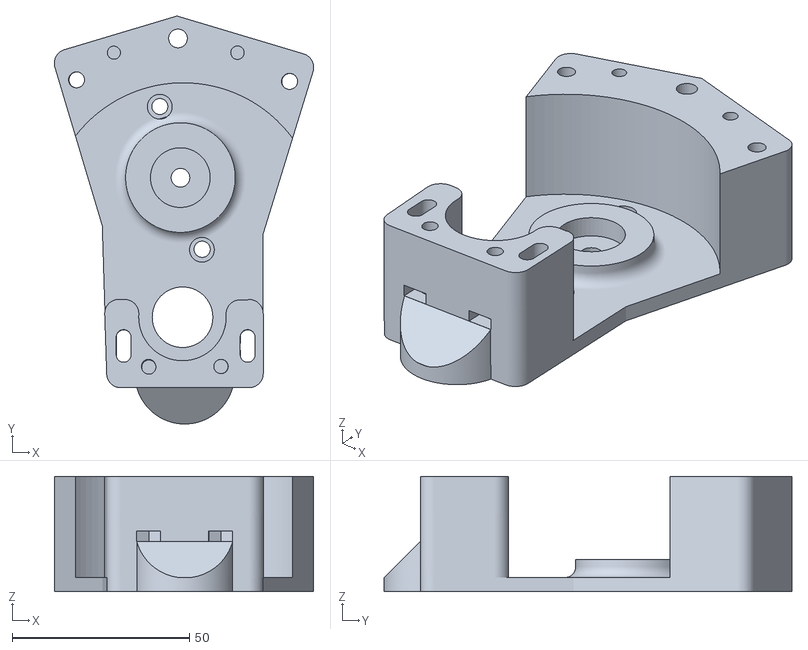
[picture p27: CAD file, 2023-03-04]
bati inférieur.stl
73.2 x 115.2 x 32.6

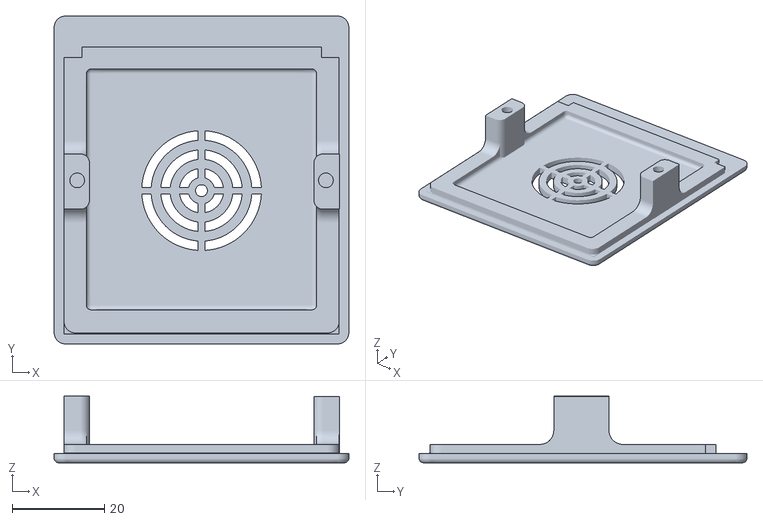
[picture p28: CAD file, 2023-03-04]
Boitier pour PCB imprimé/couvercle.stl
64.0 x 71.2 x 14.5

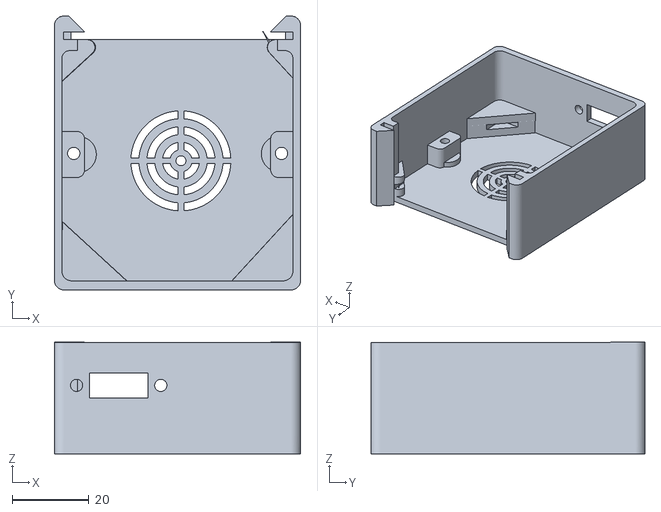
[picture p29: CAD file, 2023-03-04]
Boitier pour PCB imprimé/boitier.stl
64.0 x 71.2 x 29.1

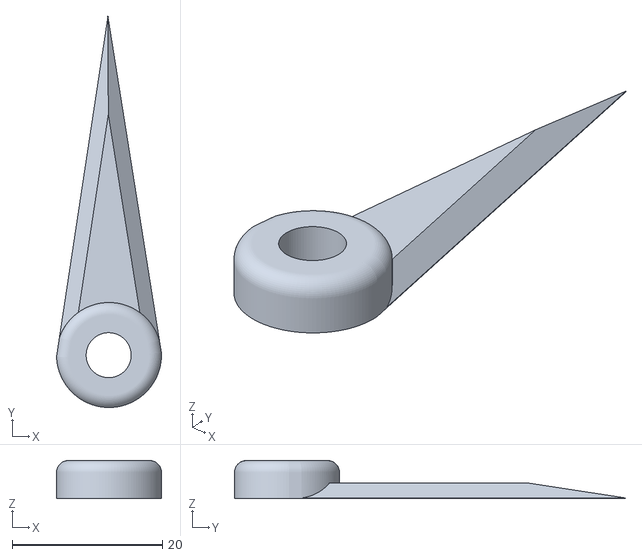
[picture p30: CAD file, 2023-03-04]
fleche.stl
14.0 x 52.1 x 5.08

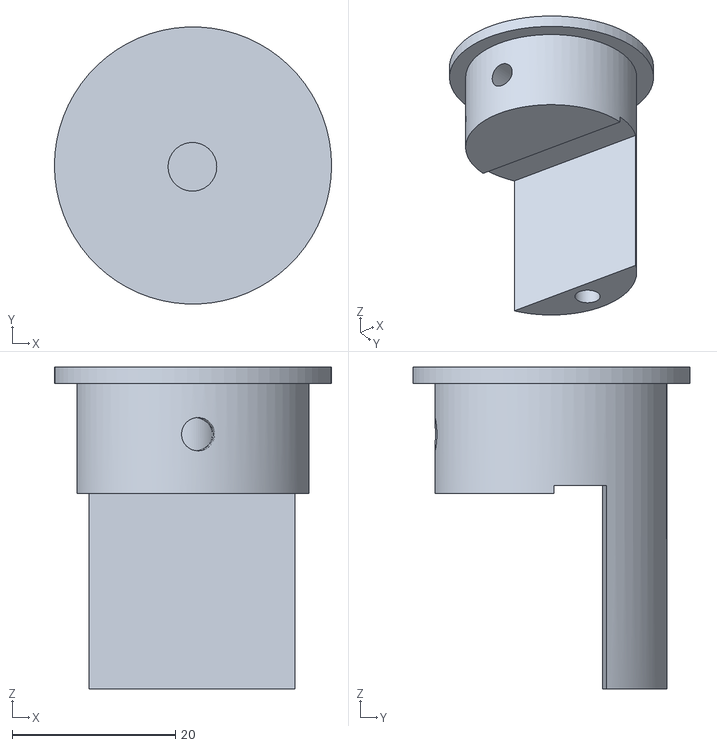
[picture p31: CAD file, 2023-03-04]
support réseau.stl
34.0 x 34.0 x 39.5

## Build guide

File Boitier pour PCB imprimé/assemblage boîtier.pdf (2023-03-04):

Assemblage du boitier recevant l'électronique.

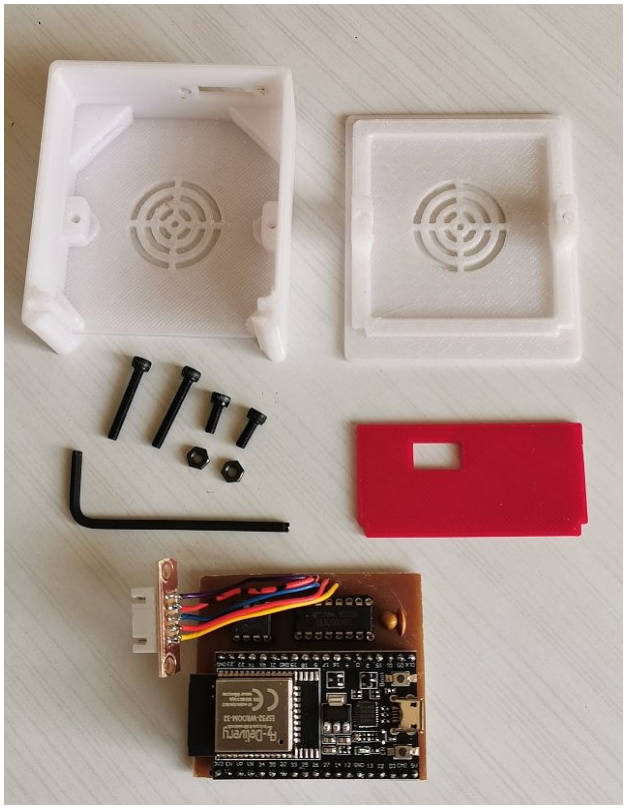
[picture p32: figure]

L'ESP32 chauffe peu, mais une bonne aération a été prévue, car les conditions d'ensoleillement lors des prises de vues peuvent être sévères. Le connecteur USB est en façade, il permet d'alimenter le montage avec un ordinateur, une alimentation secteur ou une batterie 5v. On peut envisager aussi des mises à jour du logiciel.
Le connecteur du moteur est sur la face arrière, monté sur un petit circuit imprimé. Le typon est disponible dans les fichiers proposés.
Il faudra prévoir deux vis torque d'un diamètre de 3 mm et de 20 mm de longueur, une clé Allen du même diamètre, et deux petites vis de 3 mm de diamètre et 1 cm de longueur avec leurs écrous.

L'ouverture sur la face avant de la prise USB correspond à l'ESP32 monté sur supports.

Pour le montage, on procède comme suit.

Tout d'abord, insérer le circuit imprimé dans les deux fentes prévues du côté de l'ouverture du boîtier en tenant l'ESP32 entre deux doigts, surtout sans forcer sur l'antenne qui se trouve à l'extrémité.

Puis engager le petit circuit où est soudé le connecteur, au fond du boîtier. Vissez-le, et
seulement ensuite, repoussez le circuit imprimé principal vers le fond en l'engageant dans les deux

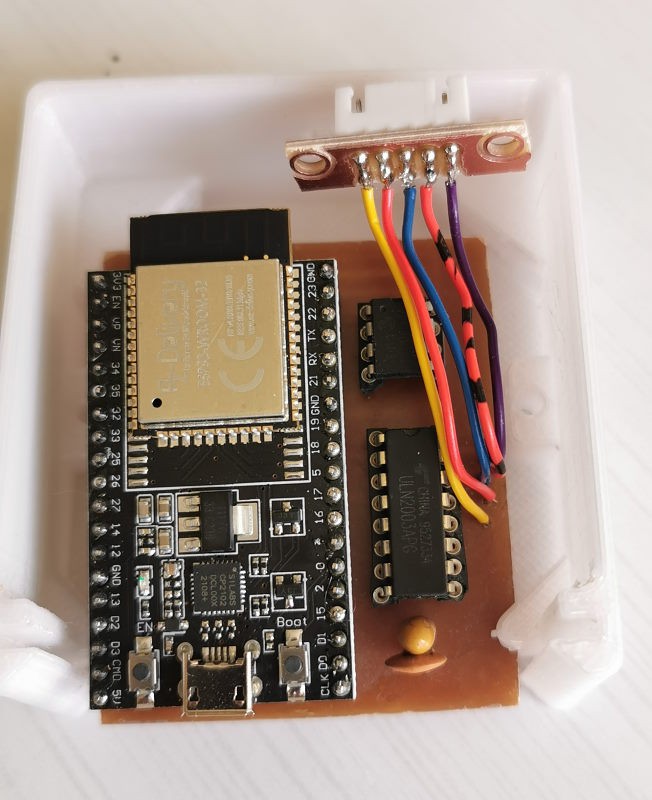
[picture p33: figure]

fentes aux deux coins. Faites attention, une des vis est proche de l'antenne de l'ESP32. Vous pouvez recouper la vis à ras de l'écrou.
Bien que cela ne perturbe pas la WIFI, des vis
en nylon peuvent être envisagées.

Rabattez les fils au-dessus du circuit imprimé principal pour ne pas gêner la fermeture du boîtier.

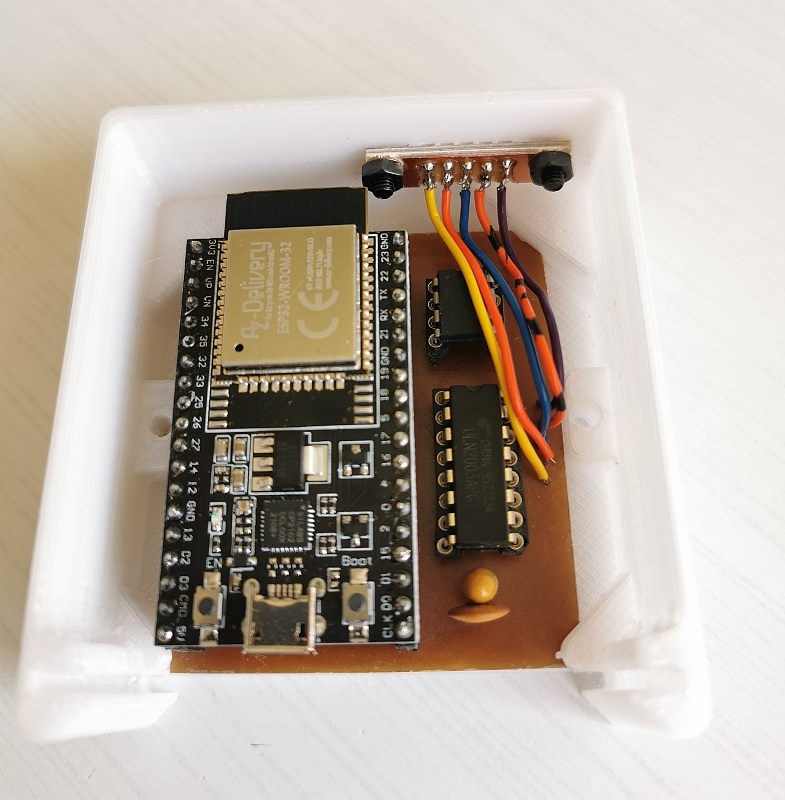
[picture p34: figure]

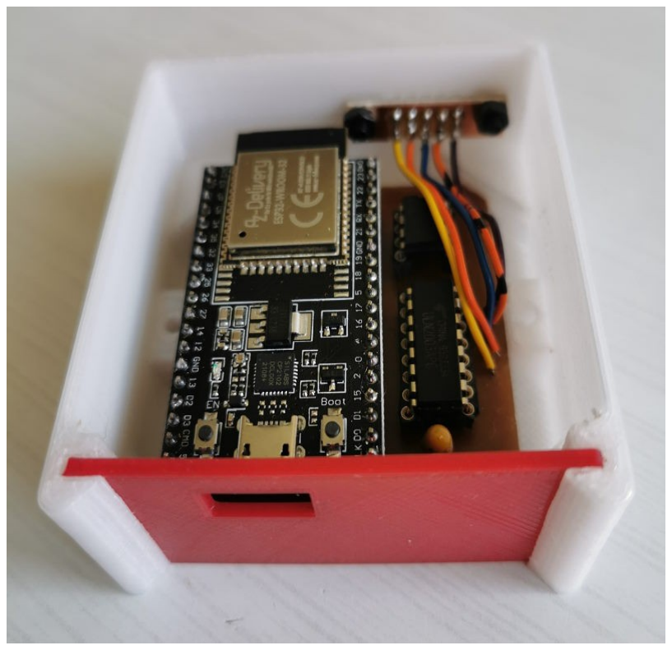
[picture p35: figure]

Fermer la face avant en la faisant glisser dans les rainures, elle va bloquer le circuit imprimé sans jeux.

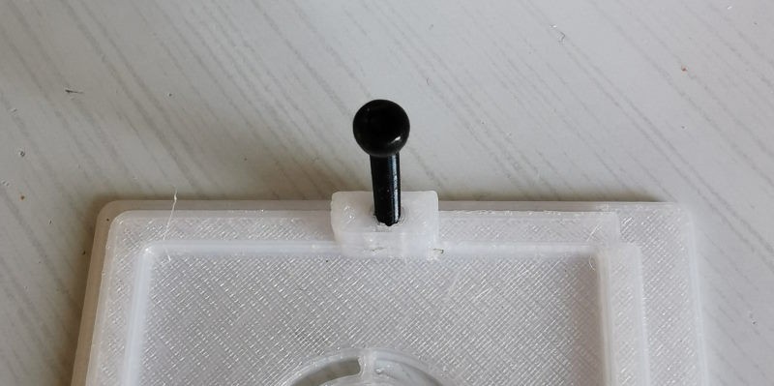
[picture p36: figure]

Il ne reste plus qu'à tarauder les plots du couvercle directement avec une vis ou mieux, avec un taraud,. Vissez par le dessous les deux vis jusqu'au blocage sans forcer.

Les têtes des vis doivent affleurer le dessous du boîtier.

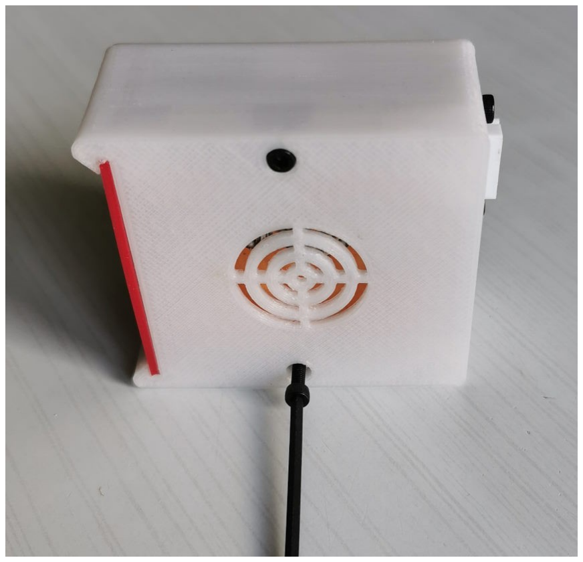
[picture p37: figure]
Jean

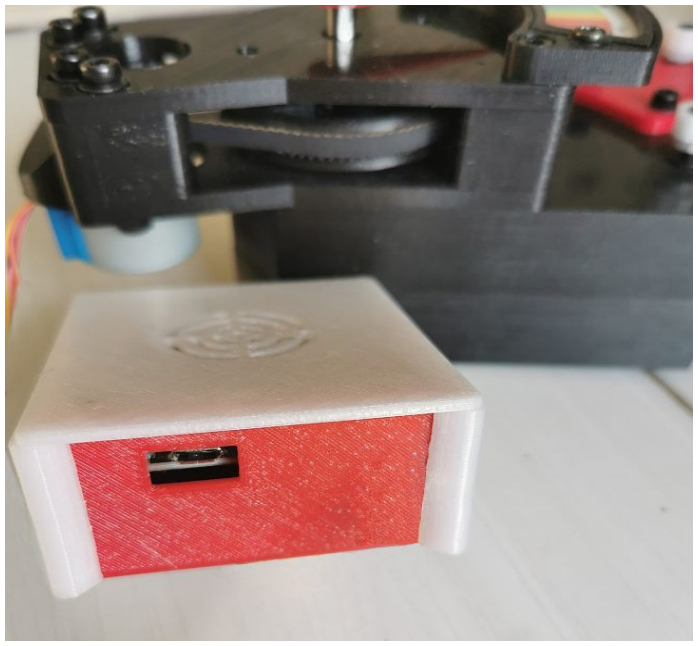
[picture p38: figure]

Et voilà, le boîtier est terminé !

Bonne réalisation à tous,
Jean Brunet

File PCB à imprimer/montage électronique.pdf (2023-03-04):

Montage du circuit imprimé

Vous trouverez dans le kit deux fichiers avec les typons des circuits imprimés au format pdf pour ceux qui souhaitent commander les circuits (voir les éventuels revendeurs sur internet) ou les graver eux-mêmes par insolation. Pour ceux qui ont une graveuse de circuit imprimé, ces fichiers sont aussi fournis au format Gerber.

Une fois en possession des circuits imprimés, on peut entamer le montage.

Prendre la platine fournie avec le moteur et retirez le circuit intégré ULN2003, dessoudez le support du circuit intégré et le connecteur blanc. Toutefois je donne une liste de tous les composants à acheter chez Conrad, qui n'est pas cher.

Commencez par souder les supports des circuits intégrés 8 broches et 16 broches, puis soudez les deux barrettes support de l'ESP32. Terminez par les deux condensateurs, attention au sens de la capacité chimique, sur la photo le positif (+) est à droite. Soudez les 5 fils en sortie de l'ULN 2003 à droite, coupés à une longueur de 45 mm.

Le connecteur est à souder dans l'alignement des deux trous des vis, détrompeur vers le haut. Les fils sont soudés directement sur les pistes du circuit.

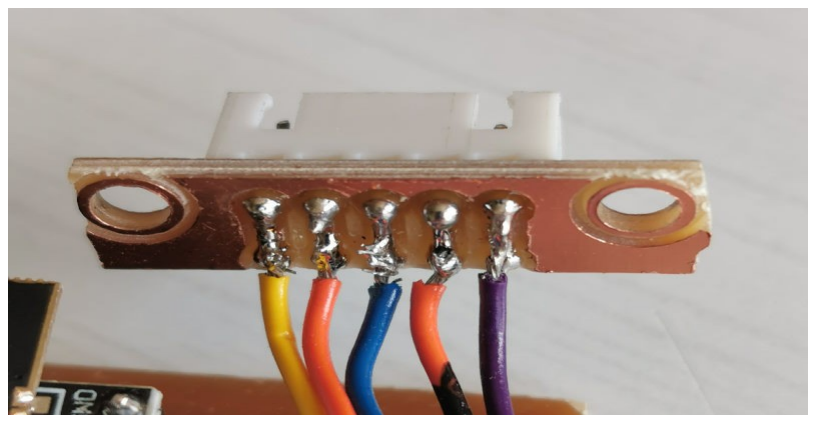
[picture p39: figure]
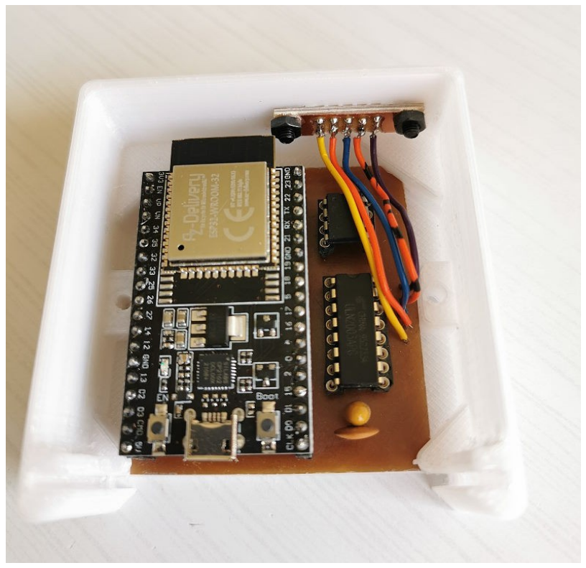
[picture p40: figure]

Bien respecter l'ordre des fils selon leur couleur. J'avais pensé souder le connecteur sur le circuit imprimé, mais ce n'est pas pratique à l'usage. On retrouve donc les liaisons dans l'ordre du connecteur.

Placez l'ULN 2003 et le 24LC01 sur leurs supports, la broche 1 est en haut à gauche. (voir ci-dessous) l'ESP32 a le connecteur USB au niveau des condensateurs.

Le circuit terminé est ici
placé dans son boitier.

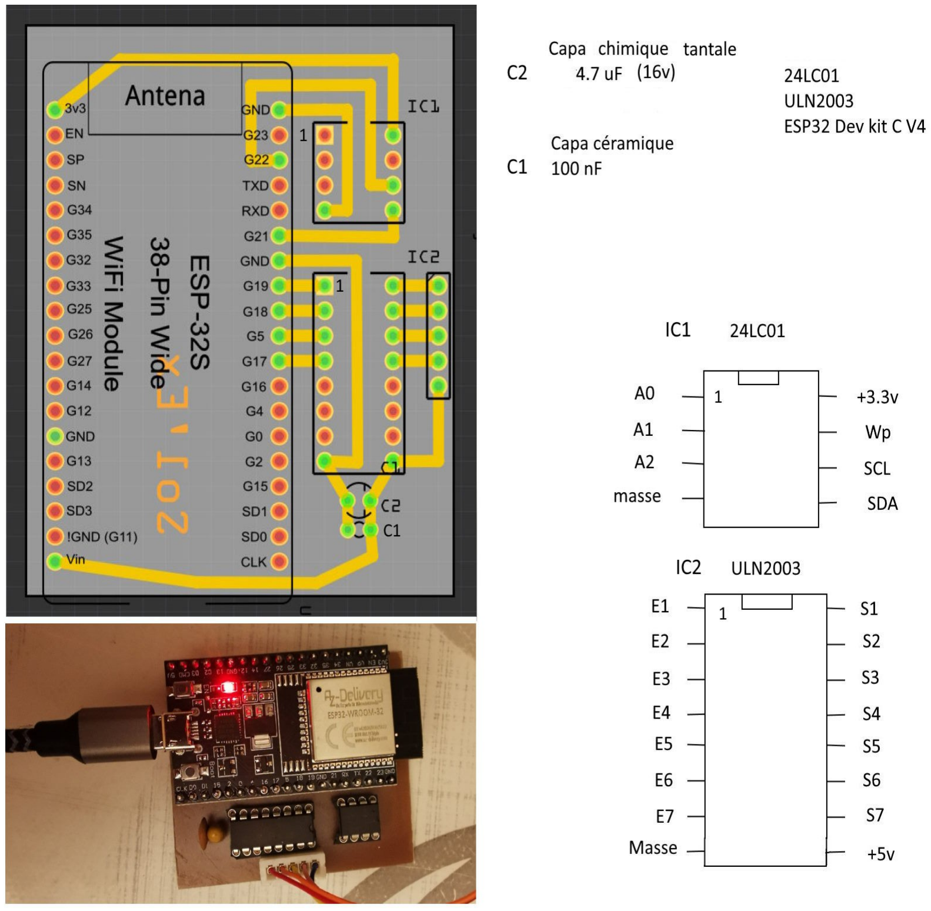
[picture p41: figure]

Fournisseur de composants : Conrad.

100 nF Condensateur céramique sortie radiale Kemet C320C104M5U5TA+ 100 nF 50 V 20 % Z5U 1 pc(s) - Conrad Electronic France (https://www.conrad.fr/fr/p/condensateur-ceramique-sortie-radiale-kemet-c320c104m5u5ta-100-nf-50-v-20-z5u-1-pc-s-1420294.html)

4,7 uF TANCAP CA42-475M035AB Condensateur tantale THT 2.5 mm 4.7 µF 35 V 20 % (l x H) 5.5 mm x 14 mm 1 pc(s) - Conrad Electronic France (https://www.conrad.fr/fr/p/tancap-ca42-475m035ab-condensateur-tantale-tht-2-5-mm-4-7-f-35-v-20-l-x-h-5-5-mm-x-14-mm-1-pc-s-1578747.html)

Support 8 broches Support de circuits intégrés 7.62 mm, 2.54 mm Nombre de pôles (num): 8 contacts de précision 1 pc(s) - Conrad Electronic France (https://www.conrad.fr/fr/p/support-de-circuits-integres-7-62-mm-2-54-mm-nombre-de-poles-num-8-contacts-de-precision-1-pc-s-189600.html)

Support 16 broches econ connect Support de circuits intégrés Nombre de pôles (num): 16 contacts de précision 1 pc(s) Tube - Conrad Electronic France (https://www.conrad.fr/fr/p/econ-connect-support-de-circuits-integres-nombre-de-poles-num-16-contacts-de-precision-1-pc-s-tube-2521065.html)

Barrettes pour l'ESP32 (en prévoir deux) Connfly Barrette femelle (standard) Nbr de rangées: 1 Nombre de pôles par rangée: 20 DS1023-1*20S21 1 pc(s) - Conrad Electronic France (https://www.conrad.fr/fr/p/connfly-barrette-femelle-standard-nbr-de-rangees-1-nombre-de-poles-par-rangee-20-ds1023-1-20s21-1-pc-s-1498265.html)

24LC01 Microchip Technology 24LC01B/P CI Mémoire DIP-8 EEPROM 1 ko 128 x 8 - Conrad Electronic France (https://www.conrad.fr/fr/p/microchip-technology-24lc01b-p-ci-memoire-dip-8-eeprom-1-ko-128-x-8-150102.html)

ULN2003 STMicroelectronics Transistor bipolaire (BJT) - Matrice ULN2003A DIP-16 7 NPN -Darlington - Conrad Electronic France (https://www.conrad.fr/fr/p/stmicroelectronics-transistor-bipolaire-bjt-matrice-uln2003a-dip-16-7-npn-darlington-177970.html)

Connecteur 5 broches Boîtier mâle (platine) econ connect W33S5 Nbr total de pôles 5 Pas: 2.5 mm 1 pc(s) - Conrad Electronic France (https://www.conrad.fr/fr/p/boitier-male-platine-econ-connect-w33s5-nbr-total-de-poles-5-pas-2-5-mm-1-pc-s-1883813.html)

Bonne réalisation à tous,
Jean Brunet

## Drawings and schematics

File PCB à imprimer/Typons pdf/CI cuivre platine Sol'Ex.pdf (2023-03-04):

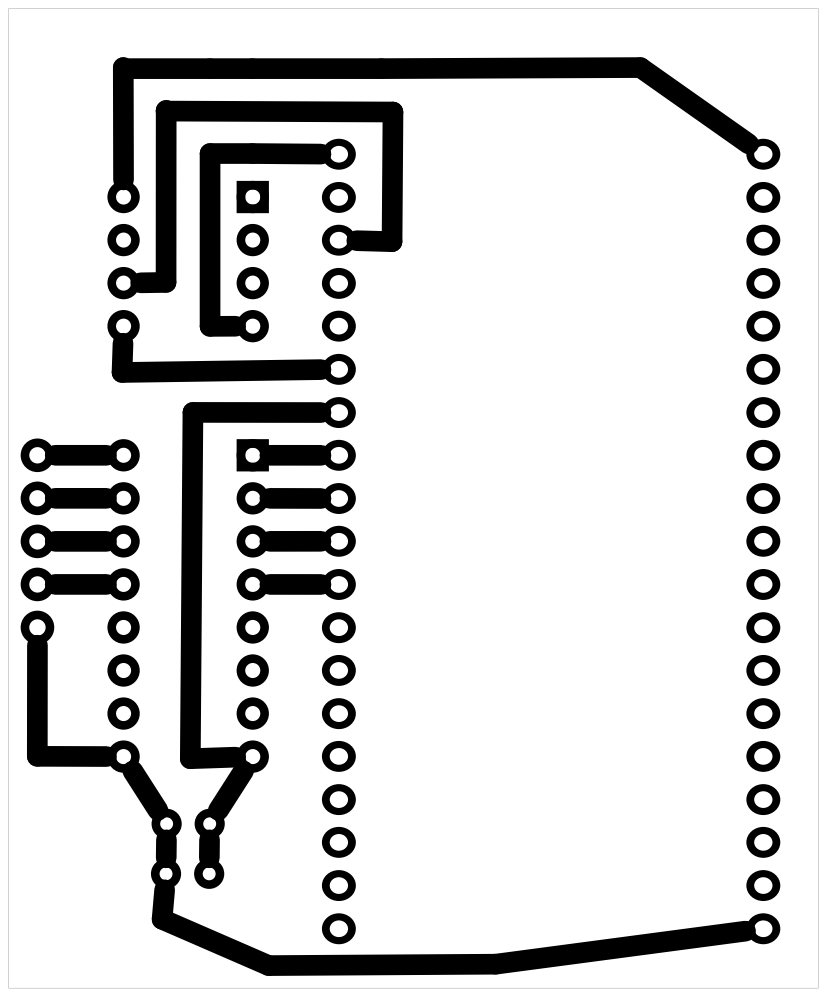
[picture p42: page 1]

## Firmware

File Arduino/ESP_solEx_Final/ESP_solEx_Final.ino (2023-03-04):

// programme de commande du réseau de Sol'Ex
// version 1.2b
// Jean Brunet  le 17/01/2023
// Modifié par Stéphane Ferier pour poulie 60 dents GT2 le 03/03/2023 avec l'accord de Jean.

#include <Wire.h>
#include <WiFi.h>

#define MOTOR_PIN_1  19   // Blue   - 28BYJ48 pin 1
#define  MOTOR_PIN_3  18  // Pink   - 28BYJ48 pin 2
#define  MOTOR_PIN_2   5  // Yellow - 28BYJ48 pin 3
#define MOTOR_PIN_4  17   //  Orange - 28BYJ48 pin 4

//#define EEPROM_SDA 23
//#define EEPROM_SCL 19
#define adresse_EEPROM 0x50   // eeprom externe 24LC01B
#define Adr1_RW_EEPROM 0
#define Adr2_RW_EEPROM 1
#define iNDICE_TABLE_RAY 30

// raies programmées
#define RAIEHalpha 1230
#define RAIENa 1060
#define RAIEMg 910
#define RAIEHb 850
#define RAIECa 670

 // rapport entre les roues 3.75 poulie 16, roue 60 en GT2
 // 2048 * 3.75 = 7680 1 tour roue
 // 1 ° = 21.333 pas, 70 ° = 1493 pas
 // conversion angströms par  pas. 1 nanomètre = 10 angströms
 // Ha à 6562.81
 // Hb à 4861.34
 // ca à 4307.74
 // sodium  5 895,924 et 5 889,950
 // Mg à 5183.62 et 5167.22

const char* ssid     = "SolEx";
const char* password = "solex1234";  // A MODIFIER si plusieurs Sol'Ex proches
WiFiServer server(80);

String header;

const unsigned int MAX_STEPS = 4000;  // limite de course du réseau
const unsigned int LITTLE_STEP = 2;  // petit déplacement
const unsigned int MIDDLE_STEP = 10;  // moyen
const unsigned int FAST_STEP = 25;    // par écran

const unsigned long STEP_DELAY_MICROSEC = 4000;  // vitesse moteur

// tableau des raies qui seront éditées dans la page web
String raies[iNDICE_TABLE_RAY] = {"y O2 898.765","Z O2 822.696","A O2 759.370","B O2 686.719","C H&#945; 656.281","a O2 627.661","D1 Na 589.592","D2 Na 588.995","D3 ou d He 587.562","e Hg 546.073","E2 Fe 527.039","b1 Mg 518.362","b2 Mg 517.270","b3 Fe 516.891","b4 Mg 516.722","c Fe 495.761","F H&#946; 486.134","d Fe 466.814","e Fe 438.355","G' ou f H&#947; 434.047","G Fe 430.790","G Ca 430.774","h H&#948; 410.175","H Ca+ 396.847","K Ca+ 393.366","L Fe 382.044","N Fe 358.121","P Ti+ 336.112","T Fe 302.108","t Ni 299.444"};
int cycle = 0;
int corrPas = 20; // correction au changement de sens, jeu des pignons
int memoSelectRaie = 4;  // indice du sélecteur de raies sur hydrogène
String fixNano = "0";
String raieString;
bool MotorFinish = true;

enum SetMotor {
  stopM = 0,
  slow = 1,
  fast = 2,
  screen = 3,
  fix = 4
} setMotor;

enum Direction {
    forward = 1,
    backward = -1
} direction;

int position = 0;
int setMove = 0;
int fixPos = 0;
unsigned long last_step_time;
int nano = 0;
bool zerofix = false;
int address = 0x50;

/* ---------------------------
setup
-------------------------------*/
void setup() 
{
    // Initialize serial port I/O.
    // Serial.begin(115200); // seulement pour déboggage
    // Initialize eeprom
   // Wire.begin(EEPROM_SDA, EEPROM_SCL);
     Wire.begin();
    // Initialize motor control pins...
    pinMode(MOTOR_PIN_1, OUTPUT);
    pinMode(MOTOR_PIN_2, OUTPUT);
    pinMode(MOTOR_PIN_3, OUTPUT);
    pinMode(MOTOR_PIN_4, OUTPUT);

    direction = forward;
    position = 0;
    last_step_time = 0L;
    WiFi.softAP(ssid, password);

    IPAddress IP = WiFi.softAPIP();
    server.begin();
     // lecture en mémoire EEPROM de la dernière position enregistrée.
    byte val1 = readbyte(adresse_EEPROM, Adr1_RW_EEPROM);
    byte val2 = readbyte(adresse_EEPROM, Adr2_RW_EEPROM);
    position = word(val1, val2);
}

/* --------------------------------
Boucle de traitement
-------------------------------------*/
void loop() 
{
	Wificommmand();  // affichage de la page web et traitement des retours utilisateur
	 // Lors de la recherche de l'ordre zéro du réseau (réglage coché dans le formulaire web), la position n'est pas actualisée. Seul le nombre de pas est modifié

}
void setupMotor()
{
	if (setMotor > stopM){  // si mouvement demandé
		if(setMotor == slow){    // si petit décalage
			setMove = LITTLE_STEP;
		}
		if(setMotor == fast){    // si moyen décalage
			setMove = MIDDLE_STEP;
		}
	   if(setMotor == screen){     // si par page d'écran 
			setMove = FAST_STEP;
		}
		if(setMotor == fix){       // nombre de pas demandé
			if(fixPos > position){  // si mouvement vers la gauche
				correctionPas(forward);  // correction du jeu des pignons
				direction = forward;
				setMove = fixPos - position;    
			}else if(fixPos < position){
				correctionPas(backward);  // correction du jeu des pignons      
				direction = backward;
				setMove = position -  fixPos;
			}
		}

		if(zerofix == false){  // réglage n'est pas coché dans le formulaire web, la position est actualisée
			if(direction == forward){
				if( position + setMove > MAX_STEPS){  // limite de course max
					setMove =  MAX_STEPS - position;
				}    
			position += setMove;   // nouvelle position
		 
			}else{
				if(position - setMove < 0){   // limite de course zéro
					setMove = position;       
				}
			position -= setMove;    // nouvelle position     
			}
		}

		commandMotor(setMove);  //  moteur actif
    raieString = convertPasNano(position);
    if(zerofix == true || position == 0 || raieString.substring(0,1) == "-"){
      raieString = "";
    }
		byte hi  = highByte(position);  // sauvegarde en eeprom de la dernière position
		byte low = lowByte(position);
		writebyte(adresse_EEPROM, Adr1_RW_EEPROM, hi);
		writebyte(adresse_EEPROM, Adr2_RW_EEPROM, low);
		setMotor = stopM;        // arrêt moteur
	}
}
/*---------------------------------------------------------------------------------------------
 Page web et traitement des commandes envoyées par l'utilisateur
------------------------------------------------------------------------------------------------*/
void Wificommmand()
{
	zerofix = false;
	WiFiClient client = server.available();   // Listen for incoming clients
   
	if (client){ 
		//Serial.println("New Client.");          // print a message out in the serial port
    while (client.connected()){            // loop while the client's connected
		if (client.available()) {             // if there's bytes to read from the client,
			char c = client.read();             // read a byte, then
			header += c;
			if (c == '\n') // si c'est la fin de la commande reçue
			{          
				client.println("HTTP/1.1 200 OK");
				client.println("Content-type:text/html");
				client.println("Connection: close");
				client.println();
        if (header.indexOf("setzero") >= 0) {  // réglage est coché, la position n'est pas actualisée
					zerofix = true;
				}
				if (header.indexOf("Left") >= 0) {
					correctionPas(backward);
					direction = backward;
					setMotor = slow;
				}else if (header.indexOf("Right") >= 0) {   // corrections manuelles de déplacement
					correctionPas(forward);
					direction = forward;
					setMotor = slow;
				 }else if (header.indexOf("fastRt") >= 0) {
				   correctionPas(forward);
					direction = forward;
					setMotor = fast;				 
				 }else if (header.indexOf("fastLt") >= 0) {
				   correctionPas(backward);
					direction = backward;
					setMotor = fast;
				 }else if (header.indexOf("screenR") >= 0) {
				   correctionPas(forward);
					direction = forward;
					setMotor = screen; 
				 }else if (header.indexOf("screenL") >= 0) {
				  correctionPas(backward);
					direction = backward;
					setMotor = screen; 
				 }else if (header.indexOf("envoi") >= 0) {   // position sur une raie donnée
         // teste les caractères, doivent être numériques et positifs
					fixNano = String(headerReturn(header,"pos"));
          
					fixPos = convertNanoPas(headerReturn(header,"pos"));
					if(fixPos >= 0){
						setMotor = fix;            
					}          
				 }else if (header.indexOf("rHa")>= 0) {  // raie H alpha
					fixPos = RAIEHalpha;  
					setMotor = fix; 
				 }else if (header.indexOf("rNa")>= 0) {  // raie Na
					fixPos = RAIENa;
					setMotor = fix; 
				 }else if (header.indexOf("rMg")>= 0) {   // raie Mg
					fixPos = RAIEMg;
					setMotor = fix; 
				 }else if (header.indexOf("rHb")>= 0) {    // raie H beta
					fixPos = RAIEHb;
					setMotor = fix; 
				 }else if (header.indexOf("rCa")>= 0) {    // raie Ca
					fixPos = RAIECa;
					setMotor = fix; 
				 }else if (header.indexOf("ordreZ")>= 0) {  // pour fixer l'ordre 0
            if (zerofix == false){   // retour sur pas 0, soit ordre zero, réglage est décoché
              fixPos = 0;  // retour sur zéro
              setMotor = fix;
            } else{
              fixPos = 0;  // on fixe la position à l'ordre zéro.
              position = 0;
            }         				
				 }else if (header.indexOf("select")>= 0) {  // raie sélectionnée dans la liste de raies
					// extrait longueur d'onde en nm
				   String nom = "tab";
				   int addr_start = header.indexOf(nom + "=")+ nom.length() + 1;
				   int addr_end = header.indexOf("&",addr_start);
				   if(addr_end == -1){
						addr_end = header.length();
				   }
				   String id = header.substring(addr_start, addr_end) ;  // indice du tableau raies retourné par le formulaire
				   int idInt = id.toInt();
				   memoSelectRaie = idInt;  // pour affichage dans formulaire le SELECT
				   int lg = raies[idInt].length();  
				   String mem = raies[idInt].substring(lg - 7,lg);
				   nano = mem.toFloat();   
				   fixPos = convertNanoPas(nano);    // donnée converties du nano en pas moteur.
				   setMotor = fix; 
				}
        //correctionPas(direction);
       // while(MotorFinish == false){}   // attend que la course moteur soit terminée     
	      setupMotor();
       	client.println(webPage());  // page web

				// The HTTP response ends with another blank line
			 
      	client.println();
				client.stop();
				header = "";
				}
			}
		}
	}
}
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

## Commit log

2023-03-04 Motorisation Sol'Ex
    This folder contain all needed files to upgrade Christian Buil's Sol'Ex (Solar Explorer) as to motorize the grating rotation. This permit to address directly any spectral line by software.
2023-03-04 Fichiers extraits du RAR
    [Graph_02032023_Final.xlsx, boitier.stl, couvercle.stl, face.stl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]
